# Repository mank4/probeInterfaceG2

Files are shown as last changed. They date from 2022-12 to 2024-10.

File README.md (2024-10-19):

# probeInterfaceG2

probeInterfaceG2 is a USB controlled interface box for transmission and reception of digital signals on 12-pins of a 14-pin flat band cable. The pin number layout is common with [GGB Picoprobe multi-contact wedge probes](https://ggb.com/home/multi-contact-wedges/). It features galvanically isolated USB for control, adjustable logic levels from 0.65 to 3.3 V and relays for disabling unused pins. The device is controlled via IEEE 488.2 compatible SCPI commands.

Currently the following interfaces are supported:
- GPIO
- SPI

probeInterfaceG2 is licensed under GPL v3. As the case's 3D model is assumed to be (c) Hammond Manufacturing Ltd., originally obtained from https://www.hammfg.com/electronics/small-case/extruded/1455#product-tables, a script is included to download the model.

probeInterfaceG2 uses
- [tinyusb](https://github.com/hathach/tinyusb)
- [scpi-parser](https://github.com/j123b567/scpi-parser)

## Hardware Features

- Raspberry RP2040 microcontroller
  - pio cells for high-speed, unconstraint muxable IO functions
  - integrated USB for programming and IEEE 488.2 SCPI control
- 0.65V - 3.3V level shifters
  - Controllable common logic level by discrete 12-bit R-2R DAC or external input
- Relays for enabling/disabling IOs

## SCPI commands

Pin numbering is based on [GGB Picoprobe multi-contact wedge probes](https://ggb.com/home/multi-contact-wedges/) numbering scheme.

__*IDN?__

Returns device type.

__*RST__

Resets settings made and clears error.

__*CLS__

Clears error. Device stores only a single error.

__:SYSTem:ERRor[:NEXT]?__

Returns <errorNumber>,<errorDescription> as described by [Keysight](https://na.support.keysight.com/pna/help/latest/Support/SCPI_Errors.htm) and clears error.

__:SYSTem:ERRor:COUNt?__

Returns number of errors.

__:SYSTem:VERSion?__

Returns system version number.

__ECHO `<text>`__

Echos argument.

__BOOTSEL__

Reboots the pin in bootloader mode.

__IO:LEVel `<V>`__

Sets the IO level voltage.

__IO<1:12>:FUnc `<IN|OUT|CS|SCK|MISO|MOSI>`__

Sets the pins function to one of the following. IN and OUT can be used multiple times while the SPI related functions can only be used once. Pins are left in last configuration when changing SPI related functions from one pin to another. This function does not enable the according output relay.

__IO<1:12>:ENable <1|0>__

Enables or disables the relay of the corresponding IO pin.

__IO<1:12>:WRite <1|0>__

Sets an OUT configured pin high or low.

__IO<1:12>:REad__

Reads an IN configured pin and returns 0 or 1.

__SPI:TRANSfer? <binary values>__

Writes the given bytes to the SPI bus using the configured settings and returns the response of MISO as binary values.

__SPI:CPHA <1|0>__

Sets the Clock phase (CPHA) to the corresponding value.

__SPI:CPOL <1|0>__

Sets the Clock polarity (CPOL) to the corresponding value.

__SPI:BAUDrate <MHz>__

Speed of the probes SPI interface is set to defined float value in MHz.

__SPI:BAUDrate?__

Reads the speed of the currently configured baudrate as float in MHz.

## RP2040 toolchain

Assuming Windows or Ubuntu/Debian the following setup is required for compiling the firmware. For normal use this is not required, VISA drivers (on Windows) are sufficient for common use.

- Only on windows: Install WSL / Ubuntu on Windows, run `sudo apt update`
- Make sure the following packages exist: `sudo apt install cmake gcc-arm-none-eabi libnewlib-arm-none-eabi libstdc++-arm-none-eabi-newlib git build-essential`
- Clone dependencies: `git submodule init` and `git submodule update`
- Clone the [pico-sdk](https://github.com/raspberrypi/pico-sdk) into the same folder as probeInterfaceG2 and update submodules if requested by cmake in the next steps
- Create build folder in firmware and cd into. `cd fw && mkdir build && cd build`
- Then run `export PICO_SDK_PATH=../../../pico-sdk` and `cmake ..`
- Then `make -j4` (4 is the number of cores used for compilation)
- If compilation fails with USB descriptor length errors, do the following: cd into pico-sdk folder and `cd lib/tinyusb/` and then `git pull origin master`
- On Windows and Linux: Copy the uf2 onto the mass storage of the RP2040. Bootloader mode is entered by pressing the button while plugging in.
- With correctly set up udev rules: Run `../load.sh` with the RP2040 connected via USB. When not running the probeInterfaceG2 firmware ress the button while pluggin in. [udev rules](https://gist.github.com/alejoseb/c7a7b4c67f0cf665dadabb26a5a87597) for the probeInterfaceG2:
```
/etc/udev/rules.d/99-probeInterfaceG2.rules
SUBSYSTEMS=="usb", ACTION=="add", ATTRS{idVendor}=="16c0", ATTRS{idProduct}=="03e8",  MODE="0666", GROUP="usbtmc"
```

For programming hints see the [Getting started](https://datasheets.raspberrypi.com/pico/getting-started-with-pico.pdf) guide.

## Possible improvements

- Better 3.3 V overvoltage protection circuit currently realized using X0202NN
- Ethernet interface VXI11
- Integrated power supply for DUT, with high precision measurement functions and grounding feature

## Resources

- Frontend
  - Agilent E3631 Service Guide
  - HP 6114A Service Guide
  - Power Designs 5020 Service Guide
  - The Art of Electronics by Horowitz
- Microcontroller
  - [RP2040](https://www.raspberrypi.com/documentation/microcontrollers/rp2040.html), [Pi pico](https://www.raspberrypi.com/products/raspberry-pi-pico/), RP2040 Minimal Kicad reference design
  - [SCPI specifications](https://www.ivifoundation.org/specifications/default.aspx), [SCPI-99 standard](https://www.ivifoundation.org/docs/scpi-99.pdf), [SCPI library](https://github.com/j123b567/scpi-parser)
  - [tinyusb for usbtmc](https://github.com/hathach/tinyusb), [example](https://github.com/markb139/pico_logic)
- Ethernet
  - Wiznet w5500 [eval](https://www.wiznet.io/product-item/w5500-evb-pico/) [doc](https://docs.wiznet.io/Product/iEthernet/W5500/w5500-evb-pico)

## Acknowledgement

The financial support by the Federal Ministry of Education and Research of Germany in the project "Open6GHub" (grant number: 16KISK005) is acknowledged.

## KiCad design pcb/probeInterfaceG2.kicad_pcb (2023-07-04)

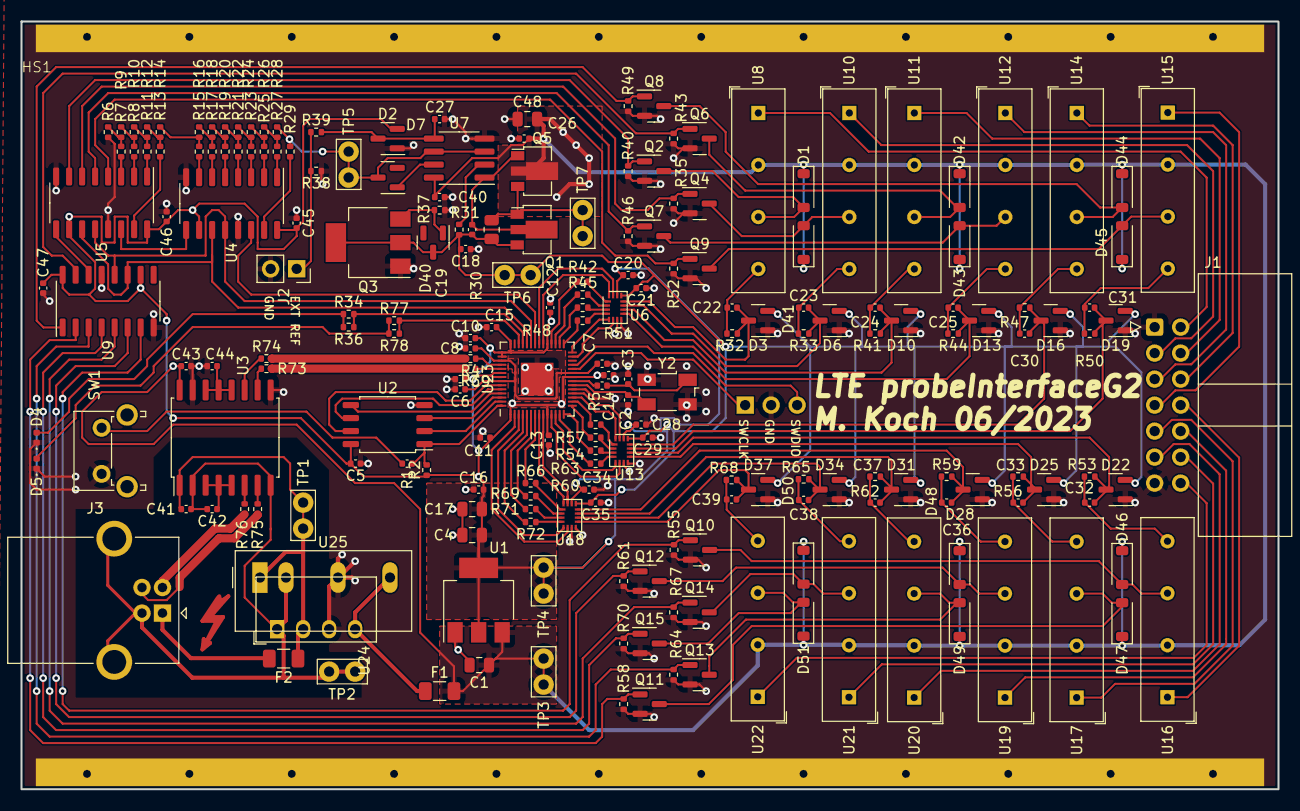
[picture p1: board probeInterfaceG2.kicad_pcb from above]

Board: 2 copper layers, 122.8 x 75.0 mm, 212 parts (1 on the bottom side), 169 nets.

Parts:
C1, C4, C17, C48: 10u; C_0805_2012Metric
C2, C3: 14p; C_0402_1005Metric
C5, C6, C7, C9, C11, C12, C13, C14, C15, C16, C20, C21, C28, C29, C34, C35, C40, C41, C42, C43, C44, C45, C46, C47: 100n; C_0402_1005Metric
C8, C10, C18, C26: 1u; C_0402_1005Metric
C19: 100p; C_0402_1005Metric
C22, C23, C24, C25, C27, C30, C31, C32, C33, C36, C37, C38, C39: 1000p; C_0402_1005Metric
D1, D41, D42, D43, D44, D45, D46, D47, D48, D49, D50, D51: 1N4148W; D_SOD-123
D2, D3, D6, D7, D10, D13, D16, D19, D22, D25, D28, D31, D34, D37: BAT54S; SOT-23
D4: LED gr; LED_0402_1005Metric
D5: LED rd; LED_0402_1005Metric
D40: BZX84C3V6; SOT-23
F1: Polyfuse 500mA; Fuse_1206_3216Metric
F2: 1A slow; Fuse_1206_3216Metric
HS1: 1455J1201
J1: Conn_02x07_Odd_Even; IDC-Header_2x07_P2.54mm_Horizontal
J2: Conn_02x01; PinSocket_1x02_P2.54mm_Vertical
J3: USB_B; USB_B_OST_USB-B1HSxx_Horizontal
J4: Debug; PinHeader_1x03_P2.54mm_Vertical
Q1, Q5: BCX56; SOT-89-3
Q2, Q4, Q6, Q7, Q8, Q9, Q10, Q11, Q12, Q13, Q14, Q15: BSS138; SOT-23
Q3: X0202NN; SOT-223
R1, R5: 1k; C_0402_1005Metric
R2, R6, R7, R8, R9, R10, R11, R12, R13, R14, R15, R16, R17, R18, R19, R20, R21, R22, R23, R24, R25, R26, R27, R28, R29, R34, R35, R36, R37, R38, R39, R40, R43, R46, R49, R52, R55, R58, R61, R64, R67, R70, R77, R78: 10k; R_0402_1005Metric
R3, R4: 27; R_0402_1005Metric
R30: 10R; R_0805_2012Metric
R31: 100R; R_0402_1005Metric
R32, R33, R41, R44, R47, R50, R53, R56, R59, R62, R65, R68: 47R; R_0402_1005Metric
R42, R45, R48, R51, R54, R57, R60, R63, R66, R69, R71, R72: 820; R_0402_1005Metric
R73, R74, R75, R76: 24R; R_0402_1005Metric
SW1: SW_Push; SW_Tactile_SPST_Angled_PTS645Vx58-2LFS
SYM1: SYM_Flash_Small; Symbol_Highvoltage_Type1_CopperTop_Small
TP1, TP2, TP3, TP4, TP5, TP6, TP7: TestPoint; TestPoint_Bridge_Pitch2.54mm_Drill1.0mm
U1: NCP1117-3.3_SOT223; SOT-223-3_TabPin2
U2: W25Q128JVS; SOIC-8_5.23x5.23mm_P1.27mm
U3: ADUM3160; SOIC-16W_7.5x10.3mm_P1.27mm
U4, U5, U9: 74HCT595; SO-16_3.9x9.9mm_P1.27mm
U6, U13, U18: SN74AXC4T774RSVR; XQFN16
U7: MCP6002-xSN; SOIC-8_3.9x4.9mm_P1.27mm
U8, U10, U11, U12, U14, U15, U16, U17, U19, U20, U21, U22: HE3621A0500; Relay_SPST_StandexMeder_SIL_Form1A
U23: RP2040; QFN-56-1EP_7x7mm_P0.4mm_EP3.2x3.2mm
U24: TBA 1-0511; Converter_DCDC_Murata_CRE1xxxxxx3C_THT
U25: TBA 2-0511; Converter_DCDC_TRACO_TMR-1-xxxx_Single_THT
Y2: 12.000MHz 12p; Crystal_SMD_Abracon_ABM3B-4Pin_5.0x3.2mm

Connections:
+1V1: C6.1, C7.1, C8.1, U23.23 (DVDD), U23.45 (VREG_VOUT), U23.50 (DVDD)
+3V3: C4.1, C5.1, C9.1, C10.1, C11.1, C12.1, C13.1, C14.1, C15.1, C16.1, C17.1, C20.1, C28.1, C34.1, C45.1, C46.1, C47.1, D2.2 (K), R2.1, TP4.1, U1.2 (VO), U2.8 (VCC), U4.10 (~SRCLR), U4.16 (VCC), U5.10 (~SRCLR), U5.16 (VCC), U6.14 (VCCA), U9.10 (~SRCLR), U9.16 (VCC), U13.14 (VCCA), U18.14 (VCCA), U23.1 (IOVDD), U23.10 (IOVDD), U23.22 (IOVDD), U23.33 (IOVDD), U23.42 (IOVDD), U23.43 (ADC_AVDD), U23.44 (VREG_IN), U23.48 (USB_VDD), U23.49 (IOVDD)
/DAC0: R7.2, U5.3 (QD)
/DAC1: R8.2, U5.2 (QC)
/DAC2: R11.2, U5.1 (QB)
/DAC3: R13.2, U5.15 (QA)
/DAC4: R15.2, U4.7 (QH)
/DAC5: R17.2, U4.6 (QG)
/DAC6: R19.2, U4.5 (QF)
/DAC7: R21.2, U4.4 (QE)
/DAC8: R23.2, U4.3 (QD)
/DAC9: R25.2, U4.2 (QC)
/DAC10: R27.2, U4.1 (QB)
/DAC11: R29.2, U4.15 (QA)
/GPIO0: U18.6 (DIR4), U23.2 (GPIO0)
/GPIO1: U18.5 (DIR3), U23.3 (GPIO1)
/GPIO2: R72.1, U23.4 (GPIO2)
/GPIO3: R71.1, U23.5 (GPIO3)
/GPIO4: R69.1, U23.6 (GPIO4)
/GPIO5: R66.1, U23.7 (GPIO5)
/GPIO6: U18.16 (DIR2), U23.8 (GPIO6)
/GPIO7: U18.15 (DIR1), U23.9 (GPIO7)
/GPIO8: U13.6 (DIR4), U23.11 (GPIO8)
/GPIO9: U13.5 (DIR3), U23.12 (GPIO9)
/GPIO10: R63.1, U23.13 (GPIO10)
/GPIO11: R60.1, U23.14 (GPIO11)
/GPIO12: R57.1, U23.15 (GPIO12)
/GPIO13: R54.1, U23.16 (GPIO13)
/GPIO14: U13.16 (DIR2), U23.17 (GPIO14)
/GPIO15: U13.15 (DIR1), U23.18 (GPIO15)
/GPIO16: U6.6 (DIR4), U23.27 (GPIO16)
/GPIO17: U6.5 (DIR3), U23.28 (GPIO17)
/GPIO18: R51.1, U23.29 (GPIO18)
/GPIO19: R48.1, U23.30 (GPIO19)
/GPIO20: R45.1, U23.31 (GPIO20)
/GPIO21: R42.1, U23.32 (GPIO21)
/GPIO22: U6.16 (DIR2), U23.34 (GPIO22)
/GPIO23: U6.15 (DIR1), U23.35 (GPIO23)
/GPIO24: U4.14 (SER), U23.36 (GPIO24)
/GPIO25: U4.12 (RCLK), U5.12 (RCLK), U9.12 (RCLK), U23.37 (GPIO25)
/GPIO26: U4.11 (SRCLK), U5.11 (SRCLK), U9.11 (SRCLK), U23.38 (GPIO26_ADC0)
/GPIO27: R34.2, R36.2, U23.39 (GPIO27_ADC1)
/GPIO28: R77.2, R78.2, U23.40 (GPIO28_ADC2)
/K1: Q2.1 (G), R40.1, U5.7 (QH)
/K2: Q4.1 (G), R35.1, U5.6 (QG)
/K3: Q6.1 (G), R43.1, U9.15 (QA)
/K4: Q7.1 (G), R46.1, U5.5 (QF)
/K5: Q8.1 (G), R49.1, U9.1 (QB)
/K6: Q9.1 (G), R52.1, U5.4 (QE)
/K7: Q10.1 (G), R55.1, U9.7 (QH)
/K8: Q11.1 (G), R58.1, U9.2 (QC)
/K9: Q12.1 (G), R61.1, U9.6 (QG)
/K10: Q13.1 (G), R64.1, U9.3 (QD)
/K11: Q14.1 (G), R67.1, U9.5 (QF)
/K12: Q15.1 (G), R70.1, U9.4 (QE)
/PP1: J1.2, U8.1
/PP2: J1.3, U10.1
/PP3: J1.4, U11.1
/PP4: J1.5, U12.1
/PP5: J1.6, U14.1
/PP6: J1.7, U15.1
/PP7: J1.8, U16.1
/PP8: J1.9, U17.1
/PP9: J1.10, U19.1
/PP10: J1.11, U20.1
/PP11: J1.12, U21.1
/PP12: J1.14, U22.1
/QSPI_SCLK: U2.6 (CLK), U23.52 (QSPI_SCLK)
/QSPI_SD0: U2.5 (DI(IO0)), U23.53 (QSPI_SD0)
/QSPI_SD1: U2.2 (DO(IO1)), U23.55 (QSPI_SD1)
/QSPI_SD2: U2.3 (IO2), U23.54 (QSPI_SD2)
/QSPI_SD3: U2.7 (IO3), U23.51 (QSPI_SD3)
/QSPI_SS: R1.1, R2.2, U2.1 (~CS), U23.56 (QSPI_SS)
/SWCLK: J4.1, U23.24 (SWCLK)
/SWDIO: J4.3, U23.25 (SWD)
/USB_D+: R3.2, R73.2
/USB_D-: R4.2, R74.2
/USBi_D+: J3.3 (D+), R75.1
/USBi_D-: J3.2 (D-), R76.1
/XIN: C2.1, U23.20 (XIN), Y2.3
/XOUT: R5.1, U23.21 (XOUT)
/dacout: D7.3 (COM), R28.2, R29.1, TP5.1, U7.3 (+), U7.6 (-)
/io1/int: C22.1, D3.3 (COM), R32.1, U6.12 (B1)
/io2/int: C23.1, D6.3 (COM), R33.1, U6.11 (B2)
/io3/int: C24.1, D10.3 (COM), R41.1, U6.10 (B3)
/io4/int: C25.1, D13.3 (COM), R44.1, U6.9 (B4)
/io5/int: C30.1, D16.3 (COM), R47.1, U13.12 (B1)
/io6/int: C31.1, D19.3 (COM), R50.1, U13.11 (B2)
/io7/int: C32.1, D22.3 (COM), R53.1, U13.10 (B3)
/io8/int: C33.1, D25.3 (COM), R56.1, U13.9 (B4)
/io9/int: C36.1, D28.3 (COM), R59.1, U18.12 (B1)
/io10/int: C37.1, D31.3 (COM), R62.1, U18.11 (B2)
/io11/int: C38.1, D34.3 (COM), R65.1, U18.10 (B3)
/io12/int: C39.1, D37.3 (COM), R68.1, U18.9 (B4)
/~USB_BOOT: R1.2, SW1.2
GND: C1.2, C2.2, C3.2, C4.2, C5.2, C6.2, C7.2, C8.2, C9.2, C10.2, C11.2, C12.2, C13.2, C14.2, C15.2, C16.2, C17.2, C18.2, C20.2, C21.2, C26.2, C27.2, C28.2, C29.2, C34.2, C35.2, C40.2, C43.2, C44.2, C45.2, C46.2, C47.2, C48.2, D2.1 (A), D3.1 (A), D4.1 (K), D5.1 (K), D6.1 (A), D10.1 (A), D13.1 (A), D16.1 (A), D19.1 (A), D22.1 (A), D25.1 (A), D28.1 (A), D31.1 (A), D34.1 (A), D37.1 (A), HS1.1, J1.1, J1.13, J2.2, J4.2, Q2.2 (S), Q3.1 (K), Q4.2 (S), Q6.2 (S), Q7.2 (S), Q8.2 (S), Q9.2 (S), Q10.2 (S), Q11.2 (S), Q12.2 (S), Q13.2 (S), Q14.2 (S), Q15.2 (S), R6.2, R31.2, R35.2, R38.1, R40.2, R43.2, R46.2, R49.2, R52.2, R55.2, R58.2, R61.2, R64.2, R67.2, R70.2, SW1.1, U1.1 (GND), U2.4 (GND), U3.9 (GND2), U3.15 (GND2), U4.8 (GND), U4.13 (~OE), U5.8 (GND), U5.13 (~OE), U6.7 (~OE), U6.8 (GND), U7.4 (V-), U9.8 (GND), U9.13 (~OE), U13.7 (~OE), U13.8 (GND), U18.7 (~OE), U18.8 (GND), U23.19 (TESTEN), U23.57 (GND), U24.3 (-Vout), U25.4 (-Vout), Y2.2, Y2.4
unnamed: C3.1, R5.2, Y2.1
unnamed: C22.2, R32.2, U8.7
unnamed: C23.2, R33.2, U10.7
unnamed: C24.2, R41.2, U11.7
unnamed: C25.2, R44.2, U12.7
unnamed: C30.2, R47.2, U14.7
unnamed: C31.2, R50.2, U15.7
unnamed: C32.2, R53.2, U16.7
unnamed: C33.2, R56.2, U17.7
unnamed: C36.2, R59.2, U19.7
unnamed: C37.2, R62.2, U20.7
unnamed: C38.2, R65.2, U21.7
unnamed: C39.2, R68.2, U22.7
unnamed: D1.2 (A), Q2.3 (D), U8.5
unnamed: C27.1, D2.3 (COM), R39.1, U7.5 (+)
unnamed: D4.2 (A), R34.1, R36.1
unnamed: D5.2 (A), R77.1, R78.1
unnamed: D7.1 (A), U7.7
unnamed: D40.1 (A), Q3.3 (G), R31.1
unnamed: D41.2 (A), Q4.3 (D), U10.5
unnamed: D42.2 (A), Q6.3 (D), U11.5
unnamed: D43.2 (A), Q7.3 (D), U12.5
unnamed: D44.2 (A), Q8.3 (D), U14.5
unnamed: D45.2 (A), Q9.3 (D), U15.5
unnamed: D46.2 (A), Q10.3 (D), U16.5
unnamed: D47.2 (A), Q11.3 (D), U17.5
unnamed: D48.2 (A), Q12.3 (D), U19.5
unnamed: D49.2 (A), Q13.3 (D), U20.5
unnamed: D50.2 (A), Q14.3 (D), U21.5
unnamed: D51.2 (A), Q15.3 (D), U22.5
unnamed: J2.1, R38.2, R39.2
unnamed: C41.2, C42.2, J3.4 (GND), J3.5 (Shield), TP2.1, U3.2 (GND1), U3.8 (GND1), U24.1 (-Vin), U25.2 (-Vin)
unnamed: F2.1, J3.1 (VBUS)
unnamed: Q1.1 (B), Q5.3 (E), R30.1, TP7.1
unnamed: C19.1, Q1.2 (C), Q5.1 (B), U7.1
unnamed: R6.1, R7.1, R9.1
unnamed: R8.1, R9.2, R10.1
unnamed: R10.2, R11.1, R12.1
unnamed: R12.2, R13.1, R14.1
unnamed: R14.2, R15.1, R16.1
unnamed: R16.2, R17.1, R18.1
unnamed: R18.2, R19.1, R20.1
unnamed: R20.2, R21.1, R22.1
unnamed: R22.2, R23.1, R24.1
unnamed: R24.2, R25.1, R26.1
unnamed: R26.2, R27.1, R28.1
unnamed: R73.1, U3.10 (DD+)
unnamed: R74.1, U3.11 (DD-)
unnamed: C42.1, U3.3 (VDD1), U3.4 (PDEN), U3.5 (SPU)
unnamed: C44.1, U3.12 (PIN), U3.13 (SPD), U3.14 (VDD2)
unnamed: R75.2, U3.7 (UD+)
unnamed: R76.2, U3.6 (UD-)
unnamed: U4.9 (QH'), U5.14 (SER)
unnamed: U5.9 (QH'), U9.14 (SER)
unnamed: R42.2, U6.1 (A1)
unnamed: R45.2, U6.2 (A2)
unnamed: R48.2, U6.3 (A3)
unnamed: R51.2, U6.4 (A4)
unnamed: R37.1, U7.2 (-)
unnamed: R54.2, U13.1 (A1)
unnamed: R57.2, U13.2 (A2)
unnamed: R60.2, U13.3 (A3)
unnamed: R63.2, U13.4 (A4)
unnamed: R66.2, U18.1 (A1)
unnamed: R69.2, U18.2 (A2)
unnamed: R71.2, U18.3 (A3)
unnamed: R72.2, U18.4 (A4)
unnamed: R4.1, U23.46 (USB_DM)
unnamed: R3.1, U23.47 (USB_DP)
unnamed: C41.1, F2.2, TP1.1, U3.1 (VBUS1), U24.2 (+Vin), U25.1 (+Vin)
unnamed: F1.2, U24.4 (+Vout), U25.6 (+Vout)
VBUS: C1.1, C26.1, C40.1, C43.1, C48.1, D1.1 (K), D41.1 (K), D42.1 (K), D43.1 (K), D44.1 (K), D45.1 (K), D46.1 (K), D47.1 (K), D48.1 (K), D49.1 (K), D50.1 (K), D51.1 (K), F1.1, Q5.2 (C), TP3.1, U1.3 (VI), U3.16 (VBUS2), U7.8 (V+), U8.3, U10.3, U11.3, U12.3, U14.3, U15.3, U16.3, U17.3, U19.3, U20.3, U21.3, U22.3
VDD: C18.1, C19.2, C21.1, C29.1, C35.1, D3.2 (K), D6.2 (K), D10.2 (K), D13.2 (K), D16.2 (K), D19.2 (K), D22.2 (K), D25.2 (K), D28.2 (K), D31.2 (K), D34.2 (K), D37.2 (K), D40.3 (K), Q1.3 (E), Q3.2 (A), Q3.4 (A), R30.2, R37.2, TP6.1, U6.13 (VCCB), U13.13 (VCCB), U18.13 (VCCB)

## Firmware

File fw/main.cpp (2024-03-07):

#include <stdlib.h>
#include <stdio.h>

#include "pico/stdlib.h"
#include "pico/bootrom.h"
#include "pio_spi.hpp"

#include "scpi/scpi.h"
#include "usbtmc_app.h"

//red led
#define PIN_LED1 28
//green led
#define PIN_LED2 27

#define PIN_REG_CLK 26
#define PIN_REG_DATA 24
#define PIN_REG_LATCH 25

#define PIN_SCK 1
#define PIN_MOSI 2
#define PIN_MISO 2 // same as MOSI, so we get loopback
#define PIN_CS 3

//waste index 0 to avoid -1 at every access
const uint8_t PIN_PP[] = {42, 21, 20, 19, 18, 13, 12, 11, 10, 5, 4, 3, 2};
const uint8_t PIN_PP_DIR[] = {42, 23, 22, 17, 16, 15, 14, 9, 8, 7, 6, 1, 0};
const uint8_t PIN_PP_SW[] = {42, 8, 9, 7, 10, 6, 11, 0, 5, 1, 4, 2, 3};

//value of register that is shifted out to the 74hc595s
static uint32_t shiftregValue = 0;

//we could add a second spi later so lets call it spi0
pioSpi spi0;


// --- shift register functions (dac and relays) ---

void shiftreg_write(uint32_t shiftData) {
    for (int i = 0; i < 24; i++) {      //loop that runs for 24 bits
        gpio_put(PIN_REG_CLK, 0);
        gpio_put(PIN_REG_DATA, shiftData & 0x1);
        shiftData >>= 1;
        sleep_us(5);
        gpio_put(PIN_REG_CLK, 1);
        sleep_us(5);
    }
    gpio_put(PIN_REG_CLK, 0);

    gpio_put(PIN_REG_LATCH, 1);
    sleep_us(5);
    gpio_put(PIN_REG_LATCH, 0);
}

void dac_set(float dacVoltage) {
    uint16_t dacValue = dacVoltage * 4095.0f / 3.3f;
    if(dacValue & 0xf000)
        dacValue = 0x0fff;
    shiftregValue = (dacValue << 12) | (shiftregValue & 0xfff);
    shiftreg_write(shiftregValue);
}

void relay_set(uint8_t ppPin, bool close) {
    shiftregValue = shiftregValue & ~(1 << PIN_PP_SW[ppPin]);
    if(close)
        shiftregValue = shiftregValue | (1 << PIN_PP_SW[ppPin]);
    shiftreg_write(shiftregValue);
    sleep_us(999);
}

// --- pp gpio functions ---

void pp_gpio_dirShifter(uint8_t ppPin, bool out) {
    gpio_init(PIN_PP_DIR[ppPin]);
    gpio_set_dir(PIN_PP_DIR[ppPin], GPIO_OUT);
    gpio_put(PIN_PP_DIR[ppPin], out);
}

void pp_gpio_dirOut(uint8_t ppPin) {
    gpio_init(PIN_PP[ppPin]);
    pp_gpio_dirShifter(ppPin, true);
    gpio_set_dir(PIN_PP[ppPin], GPIO_OUT);
    gpio_put(PIN_PP[ppPin], false);
}

void pp_gpio_dirIn(uint8_t ppPin) {
    gpio_init(PIN_PP[ppPin]);
    gpio_set_dir(PIN_PP[ppPin], GPIO_IN);
    pp_gpio_dirShifter(ppPin, false);
}

void pp_gpio_write(uint8_t ppPin, bool high) {
    gpio_put(PIN_PP[ppPin], high);
}

bool pp_gpio_read(uint8_t ppPin) {
    return (gpio_get(PIN_PP[ppPin]) != 0);
}

void pp_gpio_reset(void) {
    spi0.set_sck_pin(0);
    spi0.set_miso_pin(0);
    spi0.set_mosi_pin(0);
    spi0.set_cs_pin(0);
    spi0.set_baudrate(1);
    spi0.set_cpha(0);
    spi0.set_cpol(0);

    for(uint8_t i = 0; i <= 12; i++) {
        pp_gpio_dirIn(i);
        relay_set(i, 0);
    }
}

//###########################################
// SCPI
//###########################################

#define SCPI_ERROR_QUEUE_SIZE 17
scpi_error_t scpi_error_queue_data[SCPI_ERROR_QUEUE_SIZE];

//#define SCPI_INPUT_BUFFER_LENGTH 256
//static char scpi_input_buffer[SCPI_INPUT_BUFFER_LENGTH];

bool scpi_doIndicatorPulse = 0;
absolute_time_t scpi_doIndicatorPulseUntil;

//###########################################
// SCPI callbacks
//###########################################

static scpi_result_t pi_echo(scpi_t* context) {
    char retVal[500] = "hm";
    size_t text_len = 3;
    
    if(!SCPI_ParamCopyText(context, retVal, sizeof(retVal), &text_len, true)) {
        
    }
    
    SCPI_ResultCharacters(context, retVal, text_len);
    
    return SCPI_RES_OK;
}

static scpi_result_t pi_bootsel(scpi_t* context) {
    reset_usb_boot(PIN_LED1, 0);
    
    return SCPI_RES_OK;
}

// --- SPI callbacks ---

//syntax is #<num of byte digits><num of bytes><data>
//e.g. #18abcdefgh
static scpi_result_t pi_spi_transfer(scpi_t* context) {  
    const char* data_rx;
    size_t len = 0;
    
    if(SCPI_ParamArbitraryBlock(context, &data_rx, &len, true)) {
        char* data_tx = (char*)malloc(len);
        if(data_tx == NULL) {
            SCPI_ErrorPush(context, SCPI_ERROR_EXECUTION_ERROR);
        } else {
            spi0.enable(true);
            spi0.rw8_blocking((uint8_t*)data_rx, (uint8_t*)data_tx, len);
            spi0.enable(false);
            SCPI_ResultArbitraryBlock(context, data_tx, len);
            //SCPI_ResultArrayUInt8(context, (const uint8_t*)data, len, SCPI_FORMAT_LITTLEENDIAN);
            free(data_tx);
        }       
    } else {
        SCPI_ErrorPush(context, SCPI_ERROR_ILLEGAL_PARAMETER_VALUE);
    }
    
    return SCPI_RES_OK;
}

static scpi_result_t pi_spi_set_cpha(scpi_t* context) {
    bool value = false;
    
    if(!SCPI_ParamBool(context, &value, true)) {
        SCPI_ErrorPush(context, SCPI_ERROR_ILLEGAL_PARAMETER_VALUE);
    } else {
        spi0.set_cpha(value);
    }
    
    return SCPI_RES_OK;
}

static scpi_result_t pi_spi_set_cpol(scpi_t* context) {
    bool value = false;
    
    if(!SCPI_ParamBool(context, &value, true)) {
        SCPI_ErrorPush(context, SCPI_ERROR_ILLEGAL_PARAMETER_VALUE);
    } else {
        spi0.set_cpol(value);
    }
    
    return SCPI_RES_OK;
}

static scpi_result_t pi_spi_set_baud(scpi_t* context) {
    float value = 1.0f;
    
    if(!SCPI_ParamFloat(context, &value, true)) {
        SCPI_ErrorPush(context, SCPI_ERROR_ILLEGAL_PARAMETER_VALUE);
    } else {
        if(!spi0.set_baudrate(value)) {
            SCPI_ErrorPush(context, SCPI_ERROR_ILLEGAL_PARAMETER_VALUE);
        }
    }
    
    return SCPI_RES_OK;
}

static scpi_result_t pi_io_level(scpi_t* context) {
    float value = 1.0f;

    if(!SCPI_ParamFloat(context, &value, true)) {
        SCPI_ErrorPush(context, SCPI_ERROR_ILLEGAL_PARAMETER_VALUE);
    } else {
        if(value < 0.0f || value > 3.3f) {
            SCPI_ErrorPush(context, SCPI_ERROR_ILLEGAL_PARAMETER_VALUE);
        } else {
            dac_set(value);
        }
    }

    return SCPI_RES_OK;
}

static scpi_result_t pi_spi_get_baud(scpi_t* context) {
    SCPI_ResultFloat(context, spi0.get_baudrate());
    return SCPI_RES_OK;
}

scpi_choice_def_t pi_io_funcdef[] = {
    {"IN", 1},
    {"OUT", 2},
    {"CS", 3},
    {"SCK", 4},
    {"MISO", 5},
    {"MOSI", 6},
    SCPI_CHOICE_LIST_END
};

static scpi_result_t pi_io_func(scpi_t* context) {
    int32_t ppPin = 0;
    SCPI_CommandNumbers(context, &ppPin, 1, 0);

    int32_t choice = 0;
    if(ppPin < 1 || ppPin > 12 || !SCPI_ParamChoice(context, pi_io_funcdef, &choice, true)) {
        SCPI_ErrorPush(context, SCPI_ERROR_ILLEGAL_PARAMETER_VALUE);
    } else {
        switch(choice) {
            case 1:
                pp_gpio_dirIn(ppPin);
                break;
            case 2:
                pp_gpio_dirOut(ppPin);
                break;
            case 3:
                pp_gpio_dirShifter(ppPin, true);
                spi0.set_cs_pin(PIN_PP[ppPin]);
                break;
            case 4:
                pp_gpio_dirShifter(ppPin, true);
                spi0.set_sck_pin(PIN_PP[ppPin]);
                break;
            case 5:
                pp_gpio_dirShifter(ppPin, false);
                spi0.set_miso_pin(PIN_PP[ppPin]);
                break;
            case 6:
                pp_gpio_dirShifter(ppPin, true);
                spi0.set_mosi_pin(PIN_PP[ppPin]);
                break;
        }
    }

    return SCPI_RES_OK;
}

static scpi_result_t pi_io_enable(scpi_t* context) {
    int32_t ppPin = 0;
    SCPI_CommandNumbers(context, &ppPin, 1, 0);

    bool on = false;
    if(ppPin < 1 || ppPin > 12 || !SCPI_ParamBool(context, &on, true)) {
        SCPI_ErrorPush(context, SCPI_ERROR_ILLEGAL_PARAMETER_VALUE);
    } else {
        relay_set(ppPin, on);
    }

    return SCPI_RES_OK;
}

static scpi_result_t pi_io_write(scpi_t* context) {
    int32_t ppPin = 0;
    SCPI_CommandNumbers(context, &ppPin, 1, 0);

    bool on = false;
    if(ppPin < 1 || ppPin > 12 || !SCPI_ParamBool(context, &on, true)) {
        SCPI_ErrorPush(context, SCPI_ERROR_ILLEGAL_PARAMETER_VALUE);
    } else {
        pp_gpio_write(ppPin, on);
    }

    return SCPI_RES_OK;
}

static scpi_result_t pi_io_read(scpi_t* context) {
    int32_t ppPin = 0;
    SCPI_CommandNumbers(context, &ppPin, 1, 0);

    if(ppPin < 1 || ppPin > 12) {
        SCPI_ErrorPush(context, SCPI_ERROR_ILLEGAL_PARAMETER_VALUE);
    } else {
        bool level = pp_gpio_read(ppPin);
        SCPI_ResultBool(context, level);
    }

    return SCPI_RES_OK;
}

scpi_result_t pi_reset(scpi_t * context) {
    pp_gpio_reset();
    return SCPI_CoreRst(context);
}

//###########################################
// SCPI callback definition
//###########################################

scpi_command_t scpi_commands[] = {
    /* IEEE Mandated Commands (SCPI std V1999.0 4.1.1) */
    {"*CLS", SCPI_CoreCls, 0},
    {"*ESE", SCPI_CoreEse, 0},
    {"*ESE?", SCPI_CoreEseQ, 0},
    {"*ESR?", SCPI_CoreEsrQ, 0},
    {"*IDN?", SCPI_CoreIdnQ, 0},
    {"*OPC", SCPI_CoreOpc, 0},
    {"*OPC?", SCPI_CoreOpcQ, 0},
    //{"*RST", SCPI_CoreRst, 0},
    {"*RST", .callback = pi_reset,},
    {"*SRE", SCPI_CoreSre, 0},
    {"*SRE?", SCPI_CoreSreQ, 0},
    {"*STB?", SCPI_CoreStbQ, 0},
    {"*TST?", SCPI_CoreTstQ, 0},
    {"*WAI", SCPI_CoreWai, 0},
    
    /* Required SCPI commands (SCPI std V1999.0 4.2.1) */
    {"SYSTem:ERRor[:NEXT]?", SCPI_SystemErrorNextQ, 0},
    {"SYSTem:ERRor:COUNt?", SCPI_SystemErrorCountQ, 0},
    {"SYSTem:VERSion?", SCPI_SystemVersionQ, 0},

    //{"STATus:OPERation?", scpi_stub_callback, 0},
    //{"STATus:OPERation:EVENt?", scpi_stub_callback, 0},
    //{"STATus:OPERation:CONDition?", scpi_stub_callback, 0},
    //{"STATus:OPERation:ENABle", scpi_stub_callback, 0},
    //{"STATus:OPERation:ENABle?", scpi_stub_callback, 0},

    {"STATus:QUEStionable[:EVENt]?", SCPI_StatusQuestionableEventQ, 0},
    //{"STATus:QUEStionable:CONDition?", scpi_stub_callback, 0},
    {"STATus:QUEStionable:ENABle", SCPI_StatusQuestionableEnable, 0},
    {"STATus:QUEStionable:ENABle?", SCPI_StatusQuestionableEnableQ, 0},

    {"STATus:PRESet", SCPI_StatusPreset, 0},
    
    /* probeInterface */
    { .pattern = "ECHO", .callback = pi_echo,},
    { .pattern = "BOOTSEL", .callback = pi_bootsel,},

    { .pattern = "IO:LEVel", .callback = pi_io_level,},

    { .pattern = "IO#:FUnc", .callback = pi_io_func,},
    { .pattern = "IO#:ENable", .callback = pi_io_enable,},
    { .pattern = "IO#:WRite", .callback = pi_io_write,},
    { .pattern = "IO#:REad", .callback = pi_io_read,},

    { .pattern = "SPI:TRANSfer?", .callback = pi_spi_transfer,},
    { .pattern = "SPI:CPHA", .callback = pi_spi_set_cpha,},
    { .pattern = "SPI:CPOL", .callback = pi_spi_set_cpol,},
    { .pattern = "SPI:BAUDrate", .callback = pi_spi_set_baud,},
    { .pattern = "SPI:BAUDrate?", .callback = pi_spi_get_baud,},
    
	SCPI_CMD_LIST_END
};

scpi_t scpi_context;

size_t scpi_write(scpi_t * context, const char * data, size_t len) {
    (void) context;
    usbtmc_app_response(data, len, false);
    return len;
}

scpi_result_t scpi_flush(scpi_t* context) {
    SCPI_RegSetBits(context, SCPI_REG_STB, STB_MAV);
    usbtmc_app_response(NULL, 0, true);
    return SCPI_RES_OK;
}

scpi_interface_t scpi_interface = {
    /*.error = */ NULL,
    /*.write = */ scpi_write,
    /*.control = */ NULL,
    /*.flush = */ scpi_flush,
    /*.reset = */ NULL,
};

//###########################################
// USB callbacks
//###########################################

void usbtmc_app_query_cb(char* data, size_t len)
{
    //use usb internal buffer and SCPI_Parse
    //use scpi library for ieee488.2
    SCPI_Parse(&scpi_context, data, len);
    return;
}

uint8_t usbtmc_app_get_stb_cb(void)
{
    uint8_t status = SCPI_RegGet(&scpi_context, SCPI_REG_STB);
    SCPI_RegClearBits(&scpi_context, SCPI_REG_STB, STB_SRQ);
    return status;
}

void usbtmc_app_clear_stb_cb(void)
{
    SCPI_RegClearBits(&scpi_context, SCPI_REG_STB, 0xff);
}
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

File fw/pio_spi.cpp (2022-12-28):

/**
 * Copyright (c) 2020 Raspberry Pi (Trading) Ltd.
 *
 * SPDX-License-Identifier: BSD-3-Clause
 */

#include "pio_spi.hpp"
#include "pio_spi.pio.h"

#include "pico/stdlib.h"

pioSpi::pioSpi(PIO pio, uint sm) : pio(pio), sm(sm) {
    cpha0_prog_offs = pio_add_program(pio, &spi_cpha0_program);
    cpha1_prog_offs = pio_add_program(pio, &spi_cpha1_program);
}

pioSpi::~pioSpi() {
    pio_remove_program(pio, &spi_cpha0_program, cpha0_prog_offs);
    pio_remove_program(pio, &spi_cpha1_program, cpha1_prog_offs);
}

bool pioSpi::reset() {
    if(isEnabled)
        enable(false);
        
    sck_pin = 0;
    mosi_pin = 0;
    miso_pin = 0;
    cs_pin = 0;
    
    cpha = false;
    cpol = false;
    
    clkdiv = 31.25f; // 1 MHz @ 125 clk_sys
    
    return true;
}

bool pioSpi::set_sck_pin(uint sck) {
    if(isEnabled)
        return false;
    
    sck_pin = sck;
    return true;
}

bool pioSpi::set_mosi_pin(uint mosi) {
    if(isEnabled)
        return false;
    
    mosi_pin = mosi;
    return true;
}

bool pioSpi::set_miso_pin(uint miso) {
    if(isEnabled)
        return false;
    
    miso_pin = miso;
    return true;
}

bool pioSpi::set_cs_pin(uint cs) {
    if(isEnabled)
        return false;
    
    cs_pin = cs;
    return true;
}

bool pioSpi::set_cpha(bool _cpha) {
    if(isEnabled)
        return false;
    
    cpha = _cpha;
    return true;
}

bool pioSpi::set_cpol(bool _cpol) {
    if(isEnabled)
        return false;
    
    cpol = _cpol;
    return true;
}

bool pioSpi::set_baudrate(float baudMHz) {
    if(isEnabled)
        return false;
    
    if(baudMHz > 31.25)
        return false;
    
    if(baudMHz < 5e-4)
        return false;
        
    clkdiv = 31.25f/baudMHz;
    return true;
}

float pioSpi::get_baudrate(void) {
    return 31.25f/clkdiv;
}

bool pioSpi::enable(bool on) {
    if((on && isEnabled) || (!on && !isEnabled))
        return true;
    
    if(on) {
        pio_spi_init(pio, sm, cpha ? cpha1_prog_offs : cpha0_prog_offs,
            8,       // 8 bits per SPI frame
            clkdiv, cpha, cpol, sck_pin, mosi_pin, miso_pin);
        gpio_init(cs_pin);
        gpio_put(cs_pin, 1);
        gpio_set_dir(cs_pin, GPIO_OUT);
    } else {
        pio_sm_set_enabled(pio, sm, false);
        gpio_init_mask((1u << sck_pin) | (1u << mosi_pin) | (1u << miso_pin) | (1u << cs_pin));
        //pio_sm_set_pindirs_with_mask(pio, sm, 0, (1u << sck_pin) | (1u << mosi_pin) | (1u << miso_pin));
    }
    isEnabled = on;
    return true;
}
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

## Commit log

2022-11-12 Initial concept
    [driver.kicad_sch, probeInterfaceG2.kicad_pcb, probeInterfaceG2.kicad_sch]
2022-12-02 Added some design hints
    [driver.kicad_sch, probeInterfaceG2.kicad_sch]
2022-12-18 added spi pin setting and boot to bootsel feature
2022-12-21 added simple pcb for evaluation of level shifter
    [probeInterfaceG2.kicad_pcb, probeInterfaceG2.kicad_sch]
2022-12-26 cleaned repo and added labels to pcbSimple
    [probeInterfaceG2.kicad_pcb]
2022-12-28 add cs and example with gyro sensor
2023-01-02 simplified simplePCB
    [probeInterfaceG2.kicad_pcb, probeInterfaceG2.kicad_sch]
2023-03-06 updated schematics for bipolar supply of opamps
    [board.kicad_sch, driver.kicad_sch, probeInterfaceG2.kicad_sch]
2023-06-24 dropped psu part for simpler digital board, schematic and layout almost done
    [board.kicad_sch, driver.kicad_sch, io.kicad_sch, probeInterfaceG2.kicad_pcb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]
2023-06-25 layout done
    [probeInterfaceG2.kicad_pcb, probeInterfaceG2.kicad_sch]
2023-06-25 fixed drc
    [probeInterfaceG2.kicad_pcb, probeInterfaceG2.kicad_sch]
2023-06-25 reichelt bom added
    [io.kicad_sch, probeInterfaceG2.kicad_pcb, probeInterfaceG2.kicad_sch]
2023-07-04 added digikey bom
    [io.kicad_sch, probeInterfaceG2.kicad_pcb, probeInterfaceG2.kicad_sch]
2023-07-04 corrected digikey bom
    [io.kicad_sch, probeInterfaceG2.kicad_sch]
2023-08-31 PCB tested and firmware adapted, gpios and spi available, readme adapted, pcbSimple removed
    [probeInterfaceG2.kicad_pcb, probeInterfaceG2.kicad_sch]
